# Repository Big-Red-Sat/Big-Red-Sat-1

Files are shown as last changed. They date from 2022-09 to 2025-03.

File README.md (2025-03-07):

# Big Red Sat-1

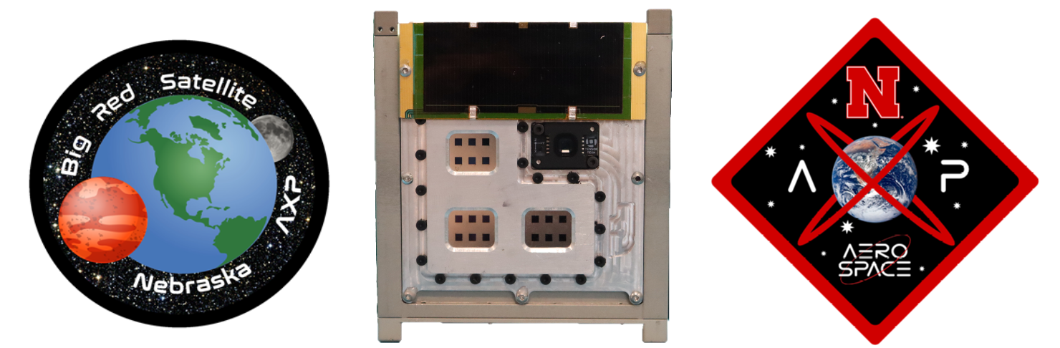
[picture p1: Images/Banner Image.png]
Banner Image


## Introduction 

This repository contains the original designs for the Big Red Sat-1 1U CubeSat, conceived, designed, and launched by a multi-disciplinary team of middle schoolers and high schoolers from the Nebraska public school system, as well as undergraduate students and graduate students from the University of Nebraska-Lincoln.  

The goal of this scientific mission is to characterize the performance and degradation of experimental perovskite solar cells from the National Renewable Energy Laboratory while in low earth orbit.  To accomplish this, a custom precision curve tracer was designed along with a low-Ohm analog multiplexer that was integrated with Near Space Launch's 1U FastBus CubeSat Platform, which incorporates an electrical power system and Iridium satellite communication system for telemetry.  

Electrical connections to the perovskite solar cell samples were made using pogo-pins, with the temperature of each sample being collected with a high-precision temperature sensor affixed to their back face with EP30-2 epoxy.  The enclosure was designed to be airtight to prevent degradation due to humidity and oxygen, so a pressure and humidity sensor were included to monitor changes in this performance.  Since the final samples had a coverslip epoxied to protect the perovskite layer, the airtight property was considered a redundancy.

Big Red Sat-1 was integrated into the Nanoracks CubeSat Deployer 27 (NRCSD27) on 12 December 2023 and launched on 21 March 2024 on the SpaceX CRS-30 mission.   

Big Red Sat-1 was deployed from NRCSD27 by Voyager Space on 18 April 2024 at 18:05:09 UTC ([Deployment Clip](https://www.youtube.com/clip/UgkxD5o3cp39FE0SL8AzyLTBCwdvlqdmNVEa)).  The satellite made first communication with the operations team at 03:00:10 UTC on 19 April 2024.  The satellite deorbited sometime after 23:41:51 UTC on 1 August 2024 after 105 days of operation.

## TLE Data

[Up to date TLE data and visualizations](https://orbit.ing-now.com/satellite/59560/1998-067wk/1998-067wk/)

## Launch Patch

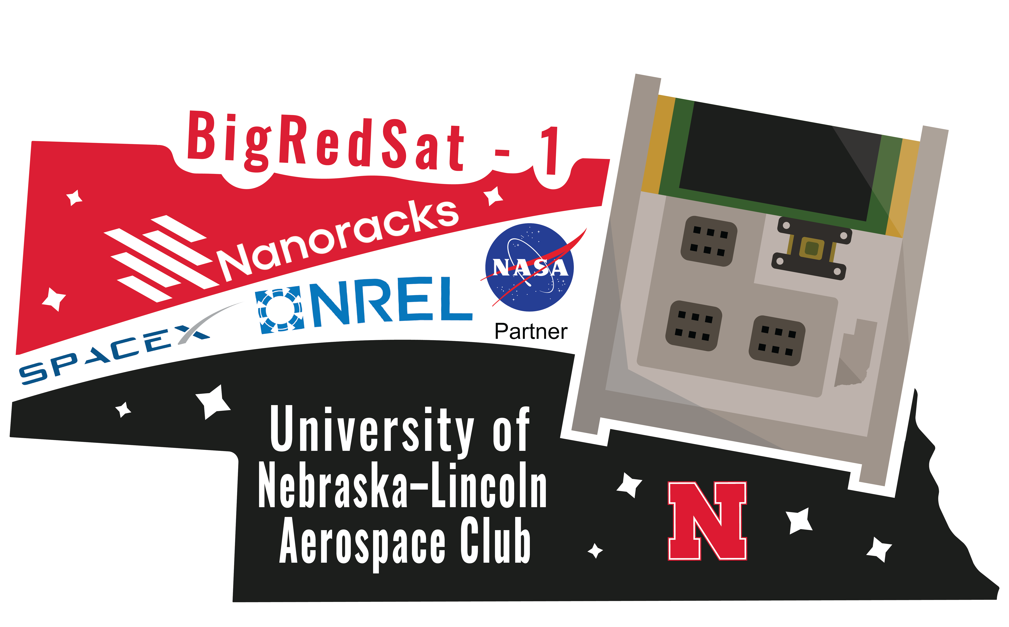
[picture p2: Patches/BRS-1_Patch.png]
BRS-1 Patch


Original concept by Morgan Hurtz, branding by Vince Orsi.

## Current Satellite Location

[SatNOGS DB - Big Red Sat-1](https://db.satnogs.org/satellite/YJQI-7143-2488-2930-9322#mapcontent)

## Prototyping Designs

- [Prototype curve tracers for high altitude balloons](https://github.com/wsarce/Big-Red-Sat-1/tree/main/Prototyping/SIV_pcb)
- [Prototype digital potentiometer curve tracer](https://github.com/wsarce/Big-Red-Sat-1/tree/main/Prototyping/singular_SIV)
- [Prototype resistor ladder curve tracer in LaunchPad form factor](https://github.com/wsarce/Big-Red-Sat-1/tree/main/Prototyping/resistor_ladder_curve_tracer)
- [Prototype analog multiplexer in LaunchPad form factor](https://github.com/wsarce/Big-Red-Sat-1/tree/main/Prototyping/perovskite_switcher/v2)
- [Pressure testing setup with ESP32 and data](https://github.com/wsarce/Big-Red-Sat-1/tree/main/Prototyping/pressure-monitor)
- [Payload breakout board to interact with perovskite cells in payload](https://github.com/wsarce/Big-Red-Sat-1/tree/main/Prototyping/payload-breakout-board/Gecko_Poker)
- [Temperature sensor prototyping](https://github.com/wsarce/Big-Red-Sat-1/tree/main/Prototyping/temp-sensor-prototyping)
- [Neopixel perovskite pixel isolator](https://github.com/wsarce/Big-Red-Sat-1/tree/main/Prototyping/perovskite-cell-isolator)
- [Prototype flight computer with curve tracer and multiplexer](https://github.com/wsarce/Big-Red-Sat-1/tree/main/Prototyping/payload_controller)
- [Magnet mounting jig for orbit alignment magnet](https://github.com/wsarce/Big-Red-Sat-1/tree/main/Prototyping/magnet_mounting)
- [Ossila AM1.5 standoff and mounts](https://github.com/wsarce/Big-Red-Sat-1/tree/main/Prototyping/ossila_mounting)
- [Tooling for building the payload](https://github.com/wsarce/Big-Red-Sat-1/tree/main/Prototyping/payload_mounting)

## Final Designs

- [Flight computer with curve tracer and analog multiplexer](https://github.com/wsarce/Big-Red-Sat-1/tree/main/Flight%20Hardware/flight_computer/v3)
- [Secondary payload with IMU and relay](https://github.com/wsarce/Big-Red-Sat-1/tree/main/Flight%20Hardware/secondary_payload)
- [Tag-Connect programming and data interface](https://github.com/wsarce/Big-Red-Sat-1/tree/main/Flight%20Hardware/Tag%20Connector)
- [Perovskite contact temperature and humiditiy sensor](https://github.com/wsarce/Big-Red-Sat-1/tree/main/Flight%20Hardware/perovskite_contact_board/V7)
- [Perovskite pogo pin board](https://github.com/wsarce/Big-Red-Sat-1/tree/main/Flight%20Hardware/perovskite_contact_board/V6/bot)
- [Perovskite payload enclosure](https://github.com/wsarce/Big-Red-Sat-1/tree/main/Flight%20Payload/Mechanical%20Design)

## Software Developed

- [NSL-EPS-Arduino, an Arduino library to communicate with the NSL electrical power system and radio](https://github.com/wsarce/NSL-EPS-Arduino)
- [FSS100-Arduino, an Arduino library to communicate with the FSS100 sun vector sensor to detect position of sun](https://github.com/wsarce/FSS100-Arduino)
- [pyOssila, a Python library to communicate with the AM1.5 sun simulator](https://github.com/wsarce/pyOssila)
- [Flight firmware for Big Red Sat-1](https://github.com/wsarce/Big-Red-Sat-1/blob/main/Flight%20Hardware/flight_computer/v3/Firmware/brs_flight_firmware/brs_flight_firmware.ino)

## Satellite Exploded View Render

https://github.com/wsarce/Big-Red-Sat-1/assets/22334349/7d4744a6-e3ca-4aac-ab56-a3370dd9aef9

### Contact
For questions, contact either Karen Stelling (kstelling2@unl.edu) or Walker Arce (wsarcera@gmail.com).

### Citation
Arce, W., & Murch-Shafer, J. (2023). Big Red Sat-1 (Version v1.0) [Computer software & hardware]. https://github.com/wsarce/Big-Red-Sat-1

### Funding and Collaboration
This work would not be possible without the generous assistance of our donors and collaborators, listed in alphabetical order below.
1.	Ameritas
2.	Acklie Charitable Foundation
3.	Cooper Foundation
4.	CubeSat Launch Initiative
5.	Ethel S. Abbott Charitable Foundation
6.	Individual Donors
7.	Millard Public Schools Foundation
8.	Monolith
9.	NASA
10.	NASA Nebraska Space Grant
11.	National Renewable Energy Laboratory
12.	Rhodes College
13.	Rodgers Foundation
14.	University of Nebraska-College of Engineering
15.	Oklahoma University

### Media

[April 21, 2021 - NASA selects Nebraska students’ satellite to orbit in space](https://news.unl.edu/newsrooms/today/article/nasa-selects-nebraska-students-satellite-to-orbit-in-space/)

[March 6, 2024 - Big Red Sat Team readies for ISS launch](https://news.unl.edu/newsrooms/today/article/big-red-sat-team-readies-for-iss-launch/)

[March 15, 2024 - Young Nebraska scientists built a satellite, it's now headed to space](https://nebraskapublicmedia.org/en/news/news-articles/young-nebraska-scientists-built-a-satellite-its-now-headed-to-space/)

[March 18, 2024 - NASA Set to Launch Four CubeSats to Space Station](https://blogs.nasa.gov/smallsatellites/2024/03/18/nasa-set-to-launch-four-cubesats-to-space-station/)

[March 21, 2024 - Nebraska students launch satellite into space](https://www.1011now.com/2024/03/21/nebraska-students-launch-satellite-into-space/)

[March 25, 2024 - NASA Space X resupply rocket launches Nebraska CubeSat into outer space](https://engineering.unl.edu/news/240325/nasa_cubesat_launch/)

[March 29, 2024 - Satellite launch a success for Nebraska Engineering team](https://news.unl.edu/newsrooms/today/article/satellite-launch-a-success-for-nebraska-engineering-team/)

[April 22, 2024 - Nebraska's first research satellite reaches International Space Station](https://www.hastingstribune.com/news/nebraskas-first-research-satellite-reaches-international-space-station/article_87f0fb4a-ffdd-11ee-b091-f7073b412070.html)

### Dataset Metadata
The following table is necessary for this dataset to be indexed by search
engines such as <a href="https://g.co/datasetsearch">Google Dataset Search</a>.
<div itemscope itemtype="http://schema.org/Dataset">
<table>
<tr>
<th>property</th>
<th>value</th>
</tr>
<tr>
<td>name</td>
<td><code itemprop="name">Big Red Sat-1 design dataset</code></td>
</tr>
<tr>
<td>description</td>
<td><code itemprop="description">The dataset and designs from the development of the Big Red Sat-1 cube satellite.</code></td>
</tr>
</tr>
<tr>
<td>url</td>
<td><code itemprop="url">https://github.com/wsarce/Big-Red-Sat-1</code></td>
</tr>
<tr>
<td>sameAs</td>
<td><code itemprop="sameAs">https://github.com/wsarce/Big-Red-Sat-1</code></td>
</tr>
<tr>
<td>citation</td>
<td><code itemprop="citation">TBA</code></td>
</tr>
<tr>
<td>hw license</td>
<td>
<div itemscope itemtype="http://schema.org/CreativeWork" itemprop="license">
<table>
<tr>
<th>property</th>
<th>value</th>
</tr>
<tr>
<td>name</td>
<td><code itemprop="name">CERN-OHL-S-2.0</code></td>
</tr>
<tr>
<td>url</td>
<td><code itemprop="url">https://spdx.org/licenses/CERN-OHL-S-2.0.html</code></td>
</tr>
</table>
</div>
</td>
</tr>
<tr>
<td>sw license</td>
<td>
<div itemscope itemtype="http://schema.org/CreativeWork" itemprop="license">
<table>
<tr>
<th>property</th>
<th>value</th>
</tr>
<tr>
<td>name</td>
<td><code itemprop="name">MIT</code></td>
</tr>
<tr>
<td>url</td>
<td><code itemprop="url">https://opensource.org/licenses/MIT</code></td>
</tr>
</table>
</div>
</td>
</tr>
<tr>
<td>docs license</td>
<td>
<div itemscope itemtype="http://schema.org/CreativeWork" itemprop="license">
<table>
<tr>
<th>property</th>
<th>value</th>
</tr>
<tr>
<td>name</td>
<td><code itemprop="name">CC BY-SA 4.0</code></td>
</tr>
<tr>
<td>url</td>
<td><code itemprop="url">https://creativecommons.org/licenses/by-sa/4.0/</code></td>
</tr>
</table>
</div>
</td>
</tr>
</table>
</div>

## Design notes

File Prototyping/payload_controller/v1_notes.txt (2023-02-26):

Each perovskite connection is 2 Ohms
------------------------
Lower resistor values do not help
------------------------
The 0 line of each BCD to decimal decoder will always be on.
To fix this, the 0 lines can be pulled, limiting the decoder to 14 perovskites
The current source and GaAs cell decoder outputs can be pulled and used 
This fix worked, only one output enabled at a time
------------------------
Switch to 4:16 decoder which have inhibit lines (CD4514BM96), tie inhibit line to current enable line
What to do with strobe line?
Break out remaining 12 outputs to an expansion header, create an expansion board that exposes 12 more panel inputs
------------------------
Separate each BCD counter reset to separate I/O pin
------------------------
The ADC clock was probably wrong(?), I used a HCMOS rather than an LVCMOS and the waveform looked terrible on the scope.
Put together new boards, ordered from JLCPCB, and test using a waveform generator and see if that fixes the ADC problems
------------------------
The op amp can't source/sink enough current to drive the panels directly
The negative voltage charge pump can't produce enough current to drive the panel input either
Likely need to use a FET with op amp for feedback to control a voltage source into the panel
I don't think this will be working in time for the cubesat
Otherwise, the DAC works well, the voltage source generation (-0.3 to 1.2) works correctly, and the charge pump works with low load.
SIT8924BA-22-33E-8.192000 is the clock used by the eval kit from TI
------------------------
I have a board that will work for the vibration testing, but I need to clear up these other problems first
------------------------

Panel 1: Cell 3
Panel 2: Cell 1
Panel 3: Cell 7
Panel 4: Cell 2
Panel 5: Cell 4
Panel 6: Cell 5
Panel 7: Cell 15
Panel 8: Cell 6
Panel 9: Cell 16

Panel 12: Cell 13
Panel 13: Cell 18
Panel 14: Cell 14
Panel 15: Cell 17
Panel 16: Cell 10
Panel 17: Cell 9
Panel 18: Cell 12
Panel 19: Cell 8
Panel 20: Cell 11

------------------------

It looks like when the COM node is the positive lead, there is influence from the other panels on the target panel.  This could probably be compensated for by connecting the bottom of the voltage divider to 3V3, so that it shifts negative voltages up to positive.  This would allow that fix.

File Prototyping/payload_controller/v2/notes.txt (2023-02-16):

Add FRAM chip to store data, calibration, etc etc.? Those chips are expensive but it may be useful for timing transmissions

Remove low pass filter on current and voltage inputs to ADC... maybe?

Create grounded border

0.5 mm box header for JTAG

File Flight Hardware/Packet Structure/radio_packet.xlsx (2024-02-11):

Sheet: Packet Structure
Byte | Primary Packet | Secondary Packet
1 | Phi MSB | Phi StD MSB |  | status register | 7 | 6 | 5 | 4 | 3 | 2 | 1 | 0
2 | Phi LSB | Phi StD LSB |  |  |  |  |  | pixel | pixel | pixel | pixel | pixel
3 | Theta MSB | Theta StD NSB
4 | Theta LSB | Theta StD LSB | Temp StD MSB
5 | Temp MSB | Rotation Rate | Temp StD LSB
6 | Temp LSB | Rotation Rate StD
7 | Status Register | Boot count | Bit 7 for relay, Bit 6 for orbit samples,
8 | Vsc | Relay Voltage |  |  |  | Multiply v and I, find max power point from trace, send point before and after that
9 | Isc | Ax
10 | V2 | Ay
11 | I2 | Az
12 | V3 | Mx
13 | I3 | My
14 | V4 | Mz
15 | I4 |  | LK99 Resistance??
16 | Voc | battery level?? | 0xBE
17 | Ioc | 0xEF
 | Write zeroes to failed fields
 | boot count should overflow in ~16 days
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

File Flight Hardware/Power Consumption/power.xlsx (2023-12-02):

Domain
3V3 | 3 | mA
VBUS | 4 | mA
VDDF | 2.8 | mA
VPP | 0.003 | mA
 | 9.803
Battery

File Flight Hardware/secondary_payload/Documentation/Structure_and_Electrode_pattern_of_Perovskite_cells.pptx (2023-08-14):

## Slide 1

Ce

Ce

MoOx (15 nm)

Au (100 nm)

Triple Cation
Perovskite Cells

Ce

Ce

MoOx (15 nm)

Au (100 nm)

Ce

SPIRO (150 nm)

Ce

SPIRO (150 nm)

Ce

Ce

Triple Cation (500 nm)

Ce

Triple Cation (500 nm)

Ce

SnO2 (50 nm)

ITO (150 nm)

Ce

Ce

SnO2 (50 nm)

ITO (150 nm)

Ce

Ce-Borosilicate (250 μm)

Ce

Fused Silica (1000 μm)

Ce

Al (100 nm)

Ce

Al (100 nm)

Ce

MoOx (15 nm)

Ce

MoOx (15 nm)

Ce

Ce

Triple Cation (500 nm)

PTAA (30 nm)

Ce

SPIRO (150 nm)

Ce

SnO2 (50 nm)

Ce

Ce

Triple Cation (500 nm)

SnO2 (50 nm)

Ce

ITO (150 nm)

Ce

ITO (150 nm)

Ce

Soda Lime Glass (1000 μm)

Ce

Soda Lime Glass (1000 μm)

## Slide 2

Ce

Ce

MoOx (15 nm)

Al (100 nm)

All-Inorganic
Perovskite Cells

Ce

Ce

MoOx (15 nm)

Au (100 nm)

Ce

PTAA (30 nm)

Ce

SPIRO (150 nm)

Ce

Ce

CsPbI2Br (250 nm)

Ce

CsPbI2Br (250 nm)

Ce

SnO2 (50 nm)

ITO (150 nm)

Ce

Ce

SnO2 (50 nm)

ITO (150 nm)

Ce

Soda Lime Glass (1000 μm)

Ce

Ce-Borosilicate (250 μm)

Ce

Au (100 nm)

Ce

Al (100 nm)

Ce

MoOx (15 nm)

Ce

MoOx (15 nm)

Ce

SPIRO (150 nm)

Ce

Ce

CsPbI2Br (250 nm)

SPIRO (150 nm)

Ce

Ce

CsPbI2Br (250 nm)

SnO2 (50 nm)

Ce

SnO2 (50 nm)

Ce

ITO (150 nm)

Ce

ITO (150 nm)

Ce

Fused Silica (1000 μm)

Ce

Soda Lime Glass (1000 μm)

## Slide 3

Electrode pattern on the solar cell

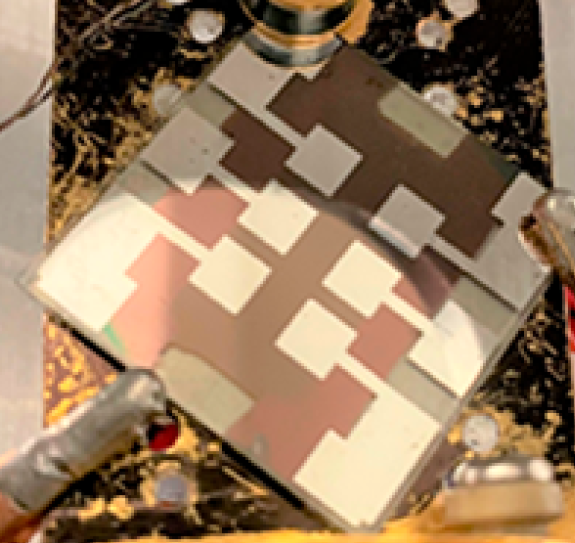
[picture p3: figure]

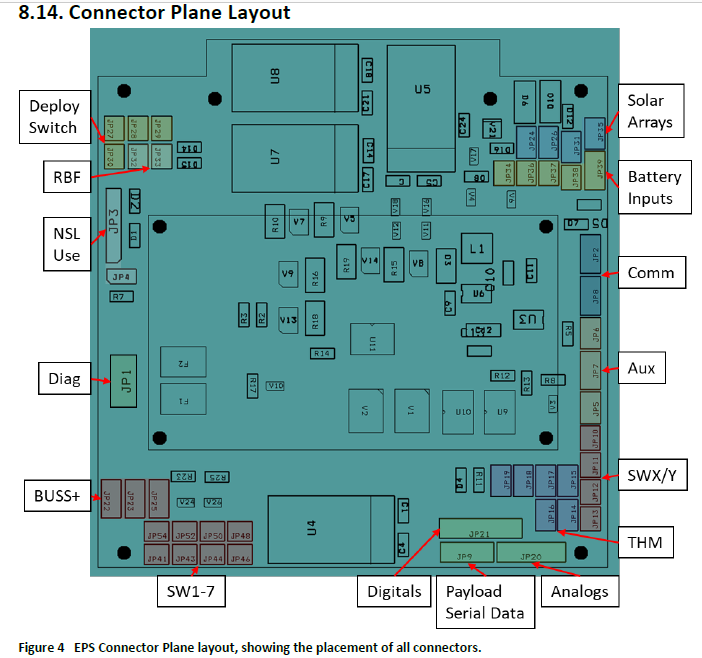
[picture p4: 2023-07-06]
Flight Hardware/secondary_payload/Documentation/Connector Specs/Connector Plane Layout.PNG

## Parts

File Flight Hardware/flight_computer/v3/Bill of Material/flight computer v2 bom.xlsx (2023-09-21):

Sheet: SMD Components
Ref | Quantity | Value | Footprint | Rating | Vendor
C1, C10, C100, C106, C109, | 5 | 10u | Capacitor_SMD:C_0603_1608Metric | AEC-Q200 | https://www.digikey.com/en/products/detail/kyocera-avx/KAM15CT70J106KT/17634162
C2, C4, C5, C6, C9, C11, C14, C15, C16, C17, C18, C19, C20, C21, C22, C23, C28, C29, C51, C52, C53, C54, C55, C56, C57, C58, C59, C60, C61, C62, C63, C64, C65, C66, C67, C68, C69, C70, C71, C74, C75, C76, C77, C78, C79, C80, C81, C82, C83, C84, C85, C86, C88, C89, C90, C91, C92, C93, C96, C97, C99, C101, C104, C107, C110, C111, | 66 | 0.1u | Capacitor_SMD:C_0603_1608Metric | COTS | https://www.digikey.com/en/products/detail/kemet/C0603T104K5RAC7867/12700990
C3, C7, C46, C47, C48, | 5 | 1u | Capacitor_SMD:C_0603_1608Metric | AEC-Q200 | https://www.digikey.com/en/products/detail/tdk-corporation/CGA3E1X7R1C105K080AC/3949775
C8, C105, C108, | 3 | 47u | Capacitor_Tantalum_SMD:CP_EIA-7343-43_Kemet-X | COTS | https://www.digikey.com/en/products/detail/kemet/T541X227M016AH6710/3478654
C12, C13, | 2 | 10p | Capacitor_SMD:C_0603_1608Metric | COTS | https://www.digikey.com/en/products/detail/kemet/C0603T100J5GAC7867/9924899
C24, C25, C26, C27, C32, C33, C34, C35, C42, | 9 | 10n | Capacitor_SMD:C_0603_1608Metric | COTS | https://www.digikey.com/en/products/detail/kemet/C0603T103K5RCL7867/2202506
FB1, | 1 | Ferrite_Bead_Small | Inductor_SMD:L_0603_1608Metric | AEC-Q200 | https://www.digikey.com/en/products/detail/tdk-corporation/MPZ1608S601ATD25/5040321
R1, R2, | 2 | 4k7 | Resistor_SMD:R_0603_1608Metric | AEC-Q200 | https://www.digikey.com/en/products/detail/vishay-dale/TNPW06034K70BEEA/1606843
R3, R71, R72, R73, R74, R75, R76, R77, R78, R80, | 10 | 10k | Resistor_SMD:R_0603_1608Metric | "Military" | https://www.digikey.com/en/products/detail/vishay-dale/TNPW060310K0FHTA/7354881
R4, R5, R6, R7, R8, R9, R14, R15, R22, R23, R24, R25, R30, R31, R42, R43, R46, | 17 | 470 | Resistor_SMD:R_0603_1608Metric | AEC-Q200 | https://www.digikey.com/en/products/detail/susumu/RG1608P-471-B-T5/1240592
R16, R17, R32, R33, R52, | 5 | 510m | Resistor_SMD:R_1206_3216Metric | AEC-Q200 | https://www.digikey.com/en/products/detail/koa-speer-electronics-inc/SR732BTTDR51J/12749611?s=N4IgTCBcDaIMoCUDsBmMAhAKpgIggrAIwBSIAugL5A
R18, R19, R20, R21, R34, R35, R36, R37, | 8 | 10M | Resistor_SMD:R_0603_1608Metric | AEC-Q200 | https://www.digikey.com/en/products/detail/vishay-dale/CRCW060310M0FHEAP/5070695
R55, R59, R63, R67, | 4 | 120 | Resistor_SMD:R_0603_1608Metric | AEC-Q200 | https://www.digikey.com/en/products/detail/susumu/RG1608N-121-W-T1/600575
R56, R60, R64, R68, | 4 | 270 | Resistor_SMD:R_0603_1608Metric | AEC-Q200 | https://www.digikey.com/en/products/detail/susumu/RG1608N-271-W-T1/600583
R57, R61, R65, R69, | 4 | 430 | Resistor_SMD:R_0603_1608Metric | AEC-Q200 | https://www.digikey.com/en/products/detail/susumu/RG1608N-431-W-T1/600588
R58, R62, R66, R70, R79, | 5 | 1M | Resistor_SMD:R_0603_1608Metric | AEC-Q200 | https://www.digikey.com/en/products/detail/rohm-semiconductor/ESR03EZPF1004/4007144
R81, | 1 | 3M | Resistor_SMD:R_0603_1608Metric | AEC-Q200 | https://www.digikey.com/en/products/detail/rohm-semiconductor/KTR03EZPF3004/4051626
Y1, | 1 | CM8V-T1A | CM8V-T1A-32:XTAL_CM8V-T1A-32.768KHZ-7PF-20PPM-TA-QC | AEC-Q200 | https://www.digikey.com/en/products/detail/jauch-quartz/Q-0-032768-JTX310-7-10-T3-HMR-LF/8108094
J5, | 1 | Panel 3 Input | Connector_Hirose:Hirose_DF13C_CL535-0403-5-51_1x03-1MP_P1.25mm_Vertical |  | https://www.digikey.com/en/products/detail/hirose-electric-co-ltd/DF13C-3P-1-25V-21/3907689
J8, | 1 | Panel 3 Output | Connector_Hirose:Hirose_DF13C_CL535-0403-5-51_1x03-1MP_P1.25mm_Vertical |  | https://www.digikey.com/en/products/detail/hirose-electric-co-ltd/DF13C-3P-1-25V-21/3907689
J9, | 1 | Sun Vector Sensor | 0781710004:MOLEX_0781710004 |  | https://www.digikey.com/en/products/detail/molex/0781710004/2424925?s=N4IgTCBcDaIOwA4CMckAYMBYQF0C%2BQA
J11, | 1 | GaAs Panel | Connector_Hirose:Hirose_DF13C_CL535-0403-5-51_1x03-1MP_P1.25mm_Vertical |  | https://www.digikey.com/en/products/detail/hirose-electric-co-ltd/DF13C-3P-1-25V-21/3907689
J12, | 1 | GaAs Temperature | Connector_Hirose:Hirose_DF13C_CL535-0403-5-51_1x03-1MP_P1.25mm_Vertical |  | https://www.digikey.com/en/products/detail/hirose-electric-co-ltd/DF13C-3P-1-25V-21/3907689
J15, J16, J18, J19, J22, | 5 | Power | Connector_Hirose:Hirose_DF13C_CL535-0402-2-51_1x02-1MP_P1.25mm_Vertical |  | https://www.digikey.com/en/products/detail/hirose-electric-co-ltd/DF13-2P-1-25V-76/9170624
J20, | 1 | BUSS+ | Connector_Hirose:Hirose_DF13C_CL535-0404-8-51_1x04-1MP_P1.25mm_Vertical |  | https://www.digikey.com/en/products/detail/hirose-electric-co-ltd/DF13C-4P-1-25V-51/3977746
J21, | 1 | EPS Serial | Connector_Hirose:Hirose_DF13C_CL535-0406-3-51_1x06-1MP_P1.25mm_Vertical |  | https://www.digikey.com/en/products/detail/hirose-electric-co-ltd/DF13B-6P-1-25V-51/3977725
Q1, Q2, Q3, | 3 | BSS138 | Package_TO_SOT_SMD:SOT-23 |  | https://www.digikey.com/en/products/detail/anbon-semiconductor-int-l-limited/BSS138/16708474
U1, U2, | 2 | OPA2387 | Package_SO:VSSOP-8_3.0x3.0mm_P0.65mm |  | https://www.digikey.com/en/products/detail/texas-instruments/OPA2387DGKR/13627209
U3, U10, | 2 | TLV7031DBV | Package_TO_SOT_SMD:SOT-23-5 |  | https://www.digikey.com/en/products/detail/texas-instruments/TLV7031DBVR/10434768?s=N4IgTCBcDaICoBkBqB2ADAZgIwBEBCSIAugL5A
U6, | 1 | CD4012BPWR | Package_SO:TSSOP-14_4.4x5mm_P0.65mm |  | https://www.digikey.com/en/products/detail/texas-instruments/CD4012BPWR/1690715
U7, | 1 | LT6654AHS6-3.3 | Package_TO_SOT_SMD:SOT-23-6 |  | https://www.digikey.com/en/products/detail/analog-devices-inc/LT6654AHS6-3-3-TRMPBF/2485815
U8, | 1 | M4FR5969SPHPT-MLS | Package_QFP:LQFP-48_7x7mm_P0.5mm | Radiation Hardened | https://www.digikey.com/en/products/detail/texas-instruments/M4FR5969SPHPT-MLS/9860026
U9, | 1 | 74CBTLV3253PW,118 | Package_SO:TSSOP-16_4.4x5mm_P0.65mm |  | https://www.digikey.com/en/products/detail/nexperia-usa-inc/74CBTLV3253PW-118/2530383
U11, U12, U13, U14, U17, | 5 | INA190A4IDDFR | ul_INA190A4IDDFR:INA190A4IDDFR |  | https://www.digikey.com/en/products/detail/texas-instruments/INA190A4IDDFR/11308738?s=N4IgTCBcDaIJIDkCCBGAnABiQFjgETwDEAlEAXQF8g
U18, U19, U20, U22, U23, U24, U25, U27, U28, U29, U30, U32, U33, U34, U35, U37, | 16 | ADG841YKSZ-500RL7 | ul_ADG841YKSZ-500RL7:ADG841YKSZ-500RL7 |  | https://www.digikey.com/en/products/detail/analog-devices-inc/ADG841YKSZ-500RL7/995409
U21, U26, U31, U36, | 4 | CD4516B_PW_16 | Package_SO:TSSOP-16_4.4x5mm_P0.65mm |  | https://www.digikey.com/en/products/detail/texas-instruments/CD4516BPW/1691567
U38, | 1 | CD4518BM96 | ul_CD4518BM96:CD4518BM96 |  | https://www.digikey.com/en/products/detail/texas-instruments/CD4520BM96/1691583
U39, | 1 | 74AHC1G08 | Package_TO_SOT_SMD:SOT-23-5 |  | https://www.digikey.com/en/products/detail/texas-instruments/SN74AHC1G08DBVR/276735
U40, U41, | 2 | CD4514BM | ul_CD4514BM:CD4514BM |  | https://www.digikey.com/en/products/detail/texas-instruments/CD4514BM/528397
U42, U43, U44, U45, U46, U47, U48, U49, U50, U51, U52, U53, U54, U55, U56, U57, U58, U59, | 18 | ADG839YKSZ-REEL7 | ul_ADG839YKSZ-REEL7:ADG839YKSZ-REEL7 |  | https://www.digikey.com/en/products/detail/analog-devices-inc/ADG839YKSZ-REEL7/995410

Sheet: THT Components
Ref | Quantity | Value | Footprint | Vendor
J10, | 1 | Perovskite 3 | Connector_Molex:Molex_PicoBlade_53047-1110_1x11_P1.25mm_Vertical | https://www.digikey.com/en/products/detail/hirose-electric-co-ltd/DF13-11P-1-25DSA-05/15997313
J13, | 1 | Perovskite 1 | Connector_Molex:Molex_PicoBlade_53047-1110_1x11_P1.25mm_Vertical | https://www.digikey.com/en/products/detail/hirose-electric-co-ltd/DF13-11P-1-25DSA-05/15997313
J14, | 1 | Perovskite 2 | Connector_Molex:Molex_PicoBlade_53047-1110_1x11_P1.25mm_Vertical | https://www.digikey.com/en/products/detail/hirose-electric-co-ltd/DF13-11P-1-25DSA-05/15997313
J3, | 1 | Secondary Payload | Connector_Molex:Molex_PicoBlade_53047-1010_1x10_P1.25mm_Vertical | https://www.digikey.com/en/products/detail/molex/0530471010/242861
J1, J2, | 2 | External Debug | Connector_Molex:Molex_PicoBlade_53047-0510_1x05_P1.25mm_Vertical | https://www.digikey.com/en/products/detail/molex/0530470510/242856

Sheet: Cable Harnesses
Item | Quantity | Length (mm) | Link
External debug cables | 2 | 100 | https://www.digikey.com/en/products/detail/molex/0151340501/6198151
Secondary payload | 1 | 100 | https://www.digikey.com/en/products/detail/molex/0151341001/7928364
Perovskite connector | 3 | 0 | https://www.digikey.com/en/products/detail/hirose-electric-co-ltd/DF13-11S-1-25C/241760

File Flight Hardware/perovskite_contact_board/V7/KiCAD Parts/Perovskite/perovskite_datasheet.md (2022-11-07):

Sourced from Oklahoma University

Exposure to oxygen and moisture will cause an increased rate of degradation

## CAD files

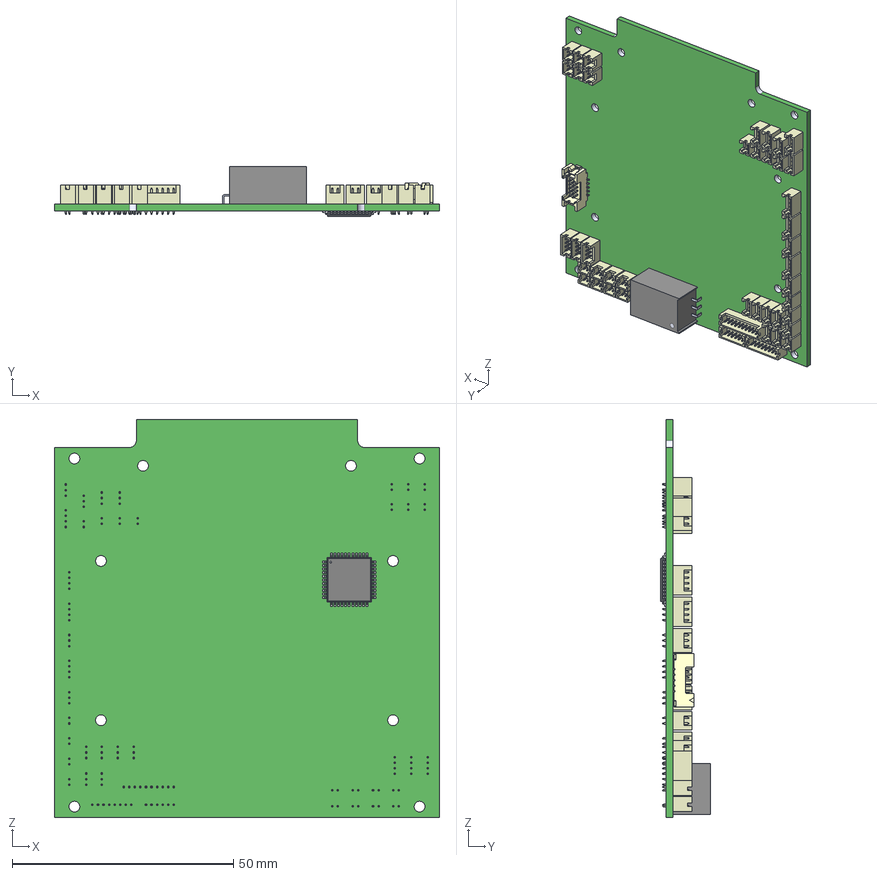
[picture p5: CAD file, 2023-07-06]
Flight Hardware/flight_computer/v3/Documentation/Connector Specs/EPS PCB Asm v17.STEP.STEP.step
87.0 x 11.3 x 90.0 mm
DF13-2P-1.25DSA.1.step.STEP x 22
DF13-3P-1.25DSA.step.STEP x 12
DF13-4P-1.25DSA.step.STEP x 7
DF13-6P-1.25DSA.step.STEP
DF13-10P-1.25DSA.step.STEP
DF13-8P-1.25DSA.step.STEP
1U EPS Board v17.step.STEP
R78B5.0-1.0L.step.STEP
DF13EA-10DP-1.25V.step.STEP
TQFP44_MC.step.STEP

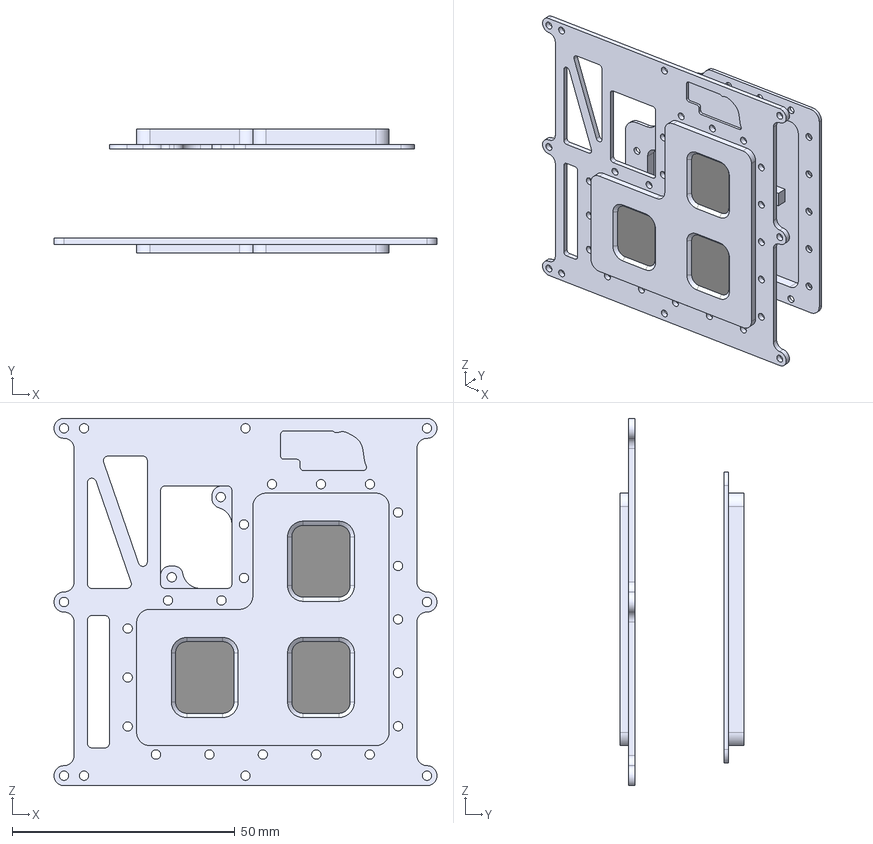
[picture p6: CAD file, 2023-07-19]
Flight Hardware/perovskite_contact_board/V7/assembly.step
86.0 x 27.9 x 82.5 mm
PayloadRedesignFinalTop
PayloadRedesignFinalBottom

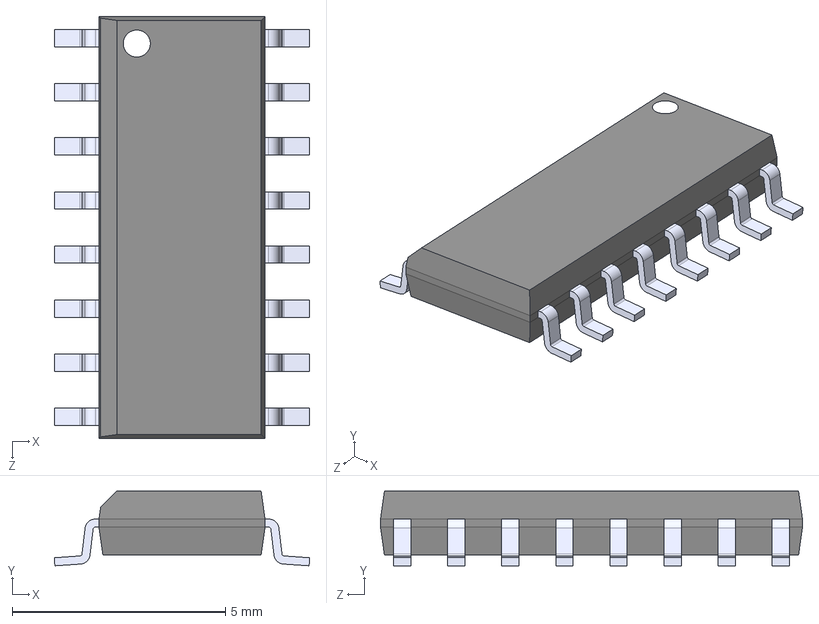
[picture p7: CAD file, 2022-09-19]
boost_converter_curve_tracer/KiCAD Parts/CD4028BMT/CD4028BMT.step
5.99 x 1.75 x 9.91 mm

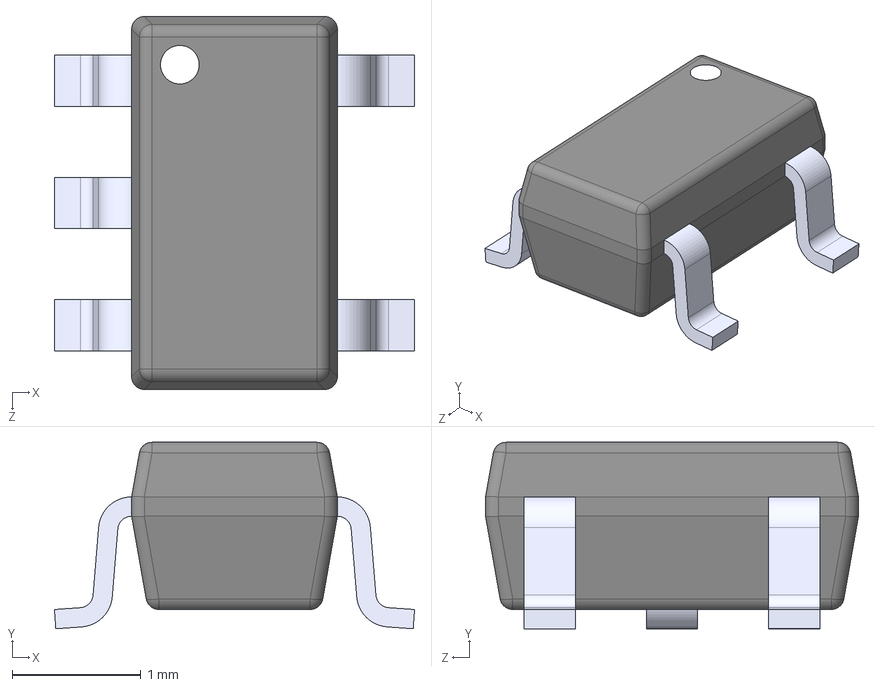
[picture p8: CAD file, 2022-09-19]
boost_converter_curve_tracer/KiCAD Parts/INA180B2IDBVT/INA180B2IDBVT.step
2.80 x 1.45 x 2.90 mm

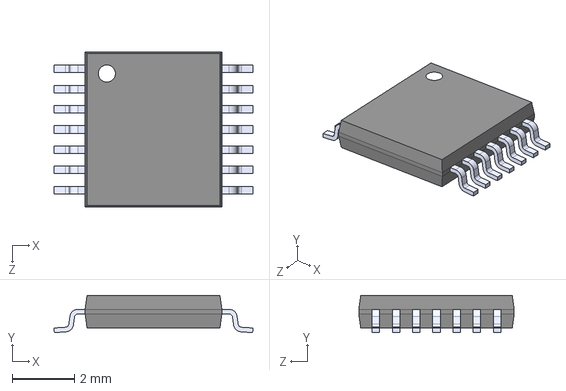
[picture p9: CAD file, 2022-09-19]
boost_converter_curve_tracer/KiCAD Parts/INA4180A4IPWR/INA4180A4IPWR.step
6.40 x 1.20 x 5.00 mm

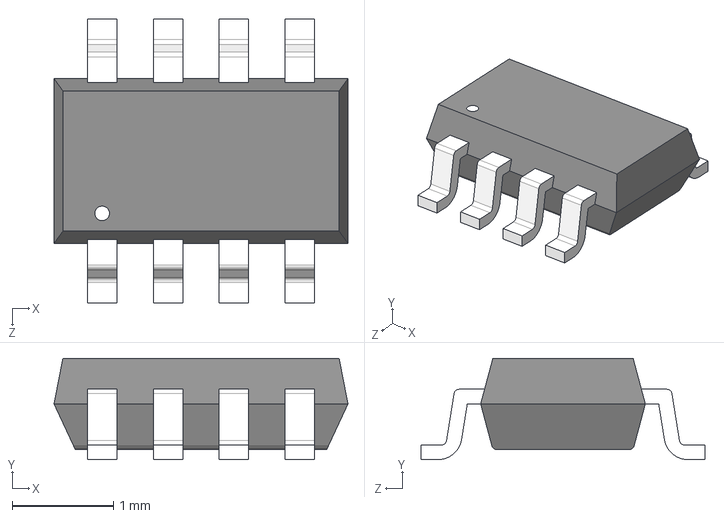
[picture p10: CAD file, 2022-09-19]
boost_converter_curve_tracer/KiCAD Parts/LT3092ETS8TRPBF/LT3092ETS8TRPBF.step
2.90 x 1.00 x 2.80 mm

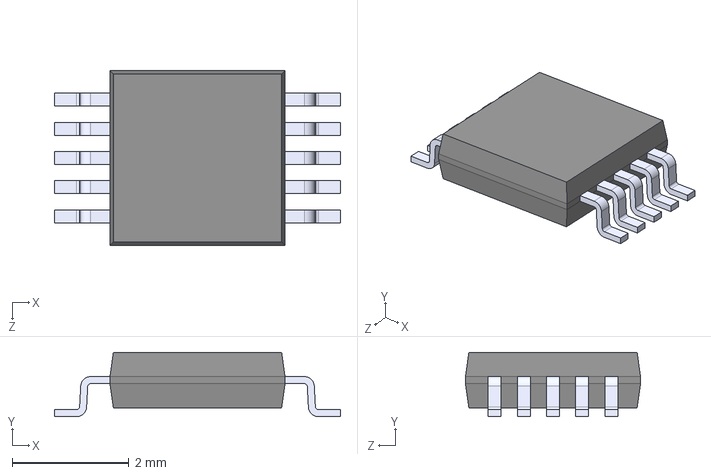
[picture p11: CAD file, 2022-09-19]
boost_converter_curve_tracer/KiCAD Parts/MAX4736EUBT/MAX4736EUBT.step
4.90 x 1.10 x 3.00 mm

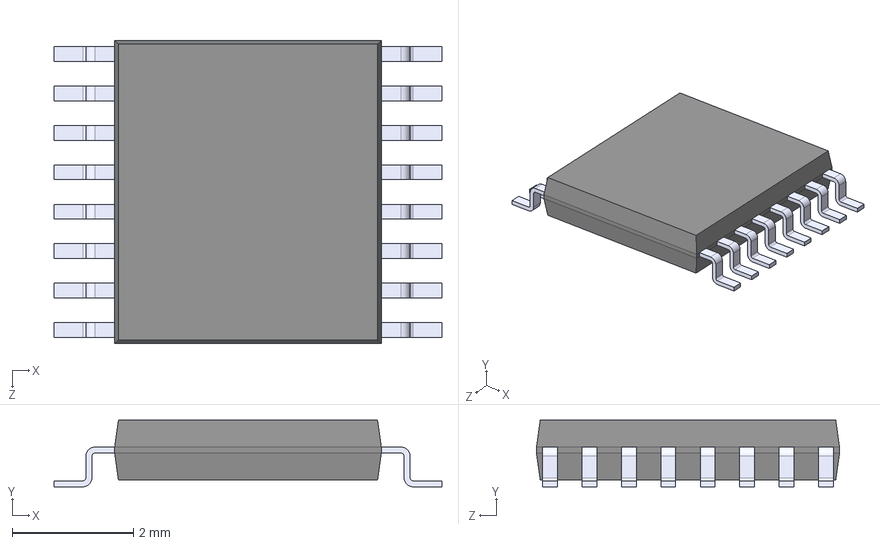
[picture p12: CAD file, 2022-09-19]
boost_converter_curve_tracer/KiCAD Parts/NX3L4051PW_118/NX3L4051PW_118.step
6.40 x 1.10 x 5.00 mm

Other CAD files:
Flight Hardware/Tag Connector/Tag Connector.step
Flight Hardware/flight_computer/v1/KiCAD Parts/LIB_G125-MH12605M4R/G125-MH12605M4R.stp
Flight Hardware/flight_computer/v1/KiCAD Parts/LIB_G125-MV12605M1P/G125-MV12605M1P.stp
Flight Hardware/flight_computer/v2/Board Outline/Cubesat_FL_Board.step
Flight Hardware/flight_computer/v2/Board Outline/final_outline.dxf
Flight Hardware/flight_computer/v2/KiCAD Parts/530471110/530471110.stp
Flight Hardware/flight_computer/v2/KiCAD Parts/LIB_G125-MH12605M4R/G125-MH12605M4R.stp
Flight Hardware/flight_computer/v2/KiCAD Parts/LIB_G125-MV12605M1P/G125-MV12605M1P.stp
Flight Hardware/flight_computer/v3/Board Outline/Cubesat_FL_Board.step
Flight Hardware/flight_computer/v3/Board Outline/final_outline.dxf
Flight Hardware/flight_computer/v3/KiCAD Parts/530471110/530471110.stp
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

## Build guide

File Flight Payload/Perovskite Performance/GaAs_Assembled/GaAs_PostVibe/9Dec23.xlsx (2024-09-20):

 | FF | VOC | JSC | Eff | ISC | MPP_V | MPP_I | MPP_P | Pixel | Sample | Direction
0 | 65.05564388 | 5728.470588 | 1.576485922 | 5.87507972 | 32.25490196 | 5.109176471 | 23.52710496 | 120.2041311 | 0 | GaAs | Reverse
1 | 72.67267267 | 5728.470588 | 1.576485922 | 6.562962412 | 32.25490196 | 5.676862745 | 23.65359477 | 134278.2109 | 0 | GaAs | Forward

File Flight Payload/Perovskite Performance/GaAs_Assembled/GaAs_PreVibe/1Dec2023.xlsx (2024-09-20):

 | FF | VOC | JSC | Eff | ISC | MPP_V | MPP_I | MPP_P | Pixel | Sample | Direction
0 | 65.82633053 | 5780.078431 | 1.576485922 | 5.99823497 | 32.25490196 | 5.160784314 | 23.78008458 | 122.7238875 | 0 | GaAs | Reverse
1 | 73.45588235 | 5780.078431 | 1.576485922 | 6.693455928 | 32.25490196 | 5.728470588 | 23.90657439 | 136948.1083 | 0 | GaAs | Forward

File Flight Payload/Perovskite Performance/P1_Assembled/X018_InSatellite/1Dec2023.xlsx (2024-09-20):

 | FF | VOC | JSC | Eff | ISC | MPP_V | MPP_I | MPP_P | Pixel | Sample | Direction
0 | 54.16666667 | 928.9411765 | 32.71288231 | 16.46035267 | 1.897347174 | 0.5031764706 | 1.897347174 | 0.9547004546 | 0 | X018 | Reverse
1 | 66.96428571 | 825.7254902 | 30.53202349 | 16.88241299 | 1.770857363 | 0.5160784314 | 1.897347174 | 979.1799534 | 0 | X018 | Forward
2 | 65.91549296 | 916.0392157 | 32.71288231 | 19.7524232 | 1.897347174 | 0.6967058824 | 1.644367551 | 1.145640545 | 1 | X018 | Reverse
3 | 87.5 | 825.7254902 | 30.53202349 | 22.05968631 | 1.770857363 | 0.7225098039 | 1.770857363 | 1279.461806 | 1 | X018 | Forward
4 | 68.6888454 | 941.8431373 | 30.53202349 | 19.7524232 | 1.770857363 | 0.6967058824 | 1.644367551 | 1.145640545 | 2 | X018 | Reverse
5 | 81.25 | 825.7254902 | 30.53202349 | 20.48399443 | 1.770857363 | 0.7225098039 | 1.644367551 | 1188.071677 | 2 | X018 | Forward
6 | 62.77665996 | 916.0392157 | 30.53202349 | 17.55770951 | 1.770857363 | 0.6709019608 | 1.517877739 | 1.018347152 | 3 | X018 | Reverse
7 | 80.87557604 | 799.9215686 | 30.53202349 | 19.7524232 | 1.770857363 | 0.6967058824 | 1.644367551 | 1145.640545 | 3 | X018 | Forward
8 | 63.98390342 | 916.0392157 | 30.53202349 | 17.89535777 | 1.770857363 | 0.6838039216 | 1.517877739 | 1.037930751 | 4 | X018 | Reverse
9 | 79.24297924 | 812.8235294 | 28.35116467 | 18.26114338 | 1.644367551 | 0.7612156863 | 1.391387928 | 1059.146316 | 4 | X018 | Forward
10 | 63.22444679 | 941.8431373 | 28.35116467 | 16.88241299 | 1.644367551 | 0.6450980392 | 1.517877739 | 0.9791799534 | 5 | X018 | Reverse
11 | 71.66276347 | 787.0196078 | 30.53202349 | 17.22006125 | 1.770857363 | 0.658 | 1.517877739 | 998.7635525 | 5 | X018 | Forward

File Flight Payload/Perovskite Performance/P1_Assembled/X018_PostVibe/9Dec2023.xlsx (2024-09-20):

 | FF | VOC | JSC | Eff | ISC | MPP_V | MPP_I | MPP_P | Pixel | Sample | Direction
0 | 65.78947368 | 980.5490196 | 26.17030585 | 16.88241299 | 1.517877739 | 0.6450980392 | 1.517877739 | 0.9791799534 | 0 | X018 | Reverse
1 | 81.94444444 | 851.5294118 | 26.17030585 | 18.26114338 | 1.517877739 | 0.7612156863 | 1.391387928 | 1059.146316 | 0 | X018 | Forward
2 | 72.07207207 | 954.745098 | 26.17030585 | 18.00790719 | 1.517877739 | 0.8257254902 | 1.264898116 | 1.044458617 | 1 | X018 | Reverse
3 | 79.88980716 | 851.5294118 | 23.98944703 | 16.31966589 | 1.391387928 | 0.7483137255 | 1.264898116 | 946.5406216 | 1 | X018 | Forward
4 | 68.18181818 | 980.5490196 | 23.98944703 | 16.03829234 | 1.391387928 | 0.7354117647 | 1.264898116 | 0.9302209557 | 2 | X018 | Reverse
5 | 79.88980716 | 851.5294118 | 23.98944703 | 16.31966589 | 1.391387928 | 0.7483137255 | 1.264898116 | 946.5406216 | 2 | X018 | Forward
6 | 65.43589744 | 967.6470588 | 28.35116467 | 17.95163248 | 1.644367551 | 0.7483137255 | 1.391387928 | 1.041194684 | 3 | X018 | Reverse
7 | 83.20512821 | 838.627451 | 26.17030585 | 18.26114338 | 1.517877739 | 0.7612156863 | 1.391387928 | 1059.146316 | 3 | X018 | Forward
8 | 71.84684685 | 954.745098 | 26.17030585 | 17.95163248 | 1.517877739 | 0.7483137255 | 1.391387928 | 1.041194684 | 4 | X018 | Reverse
9 | 74.49494949 | 851.5294118 | 26.17030585 | 16.60103944 | 1.517877739 | 0.7612156863 | 1.264898116 | 962.8602875 | 4 | X018 | Forward
10 | 59.21052632 | 980.5490196 | 26.17030585 | 15.19417169 | 1.517877739 | 0.6967058824 | 1.264898116 | 0.8812619581 | 5 | X018 | Reverse
11 | 73.92473118 | 799.9215686 | 26.17030585 | 15.47554524 | 1.517877739 | 0.7096078431 | 1.264898116 | 897.581624 | 5 | X018 | Forward

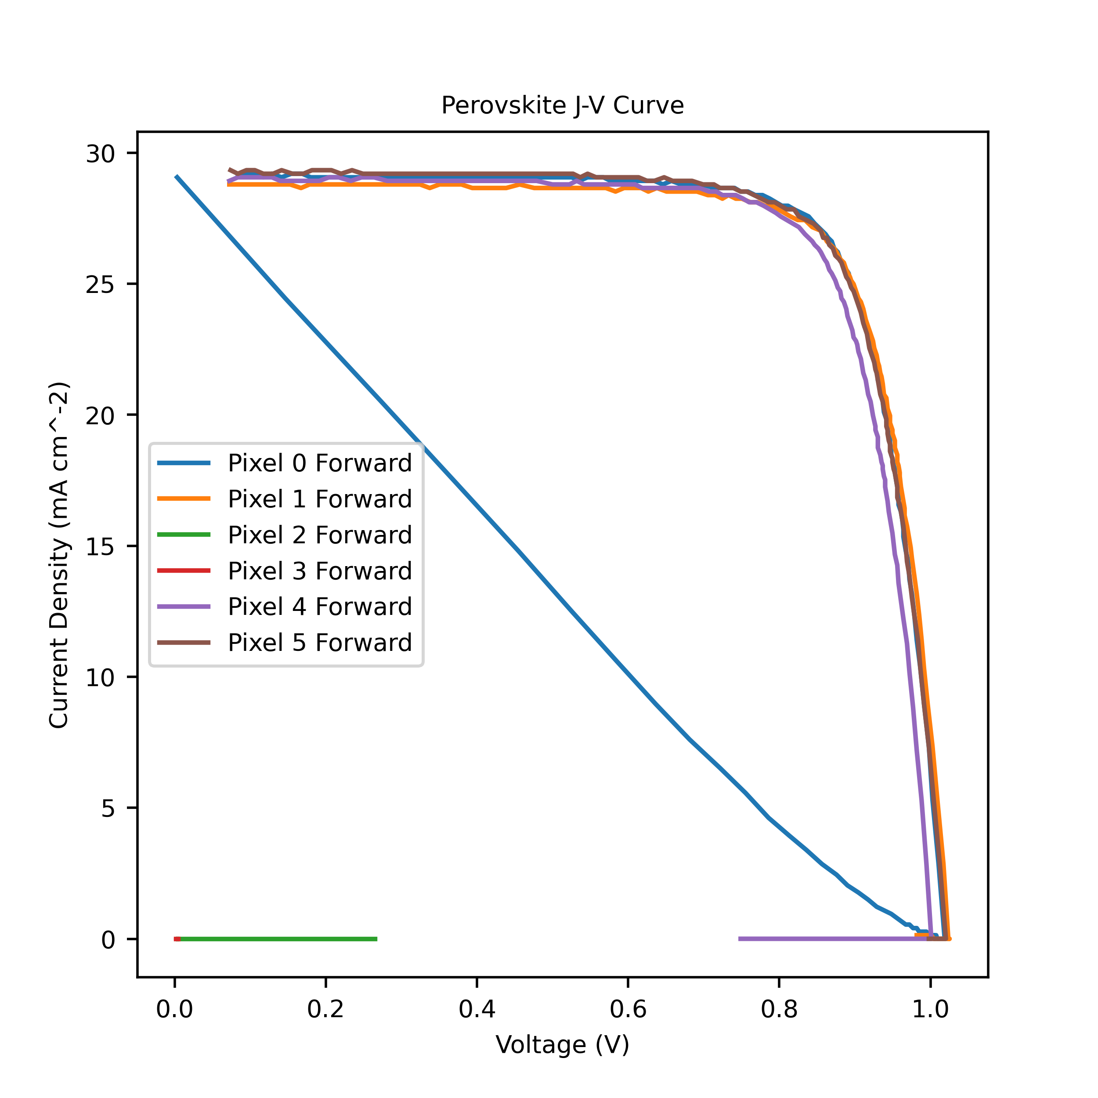
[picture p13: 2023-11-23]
Flight Payload/Perovskite Performance/P2_Assembled/X016_PreSatellite/X016_Payload2_FinalCurves_plotted_Forward.png

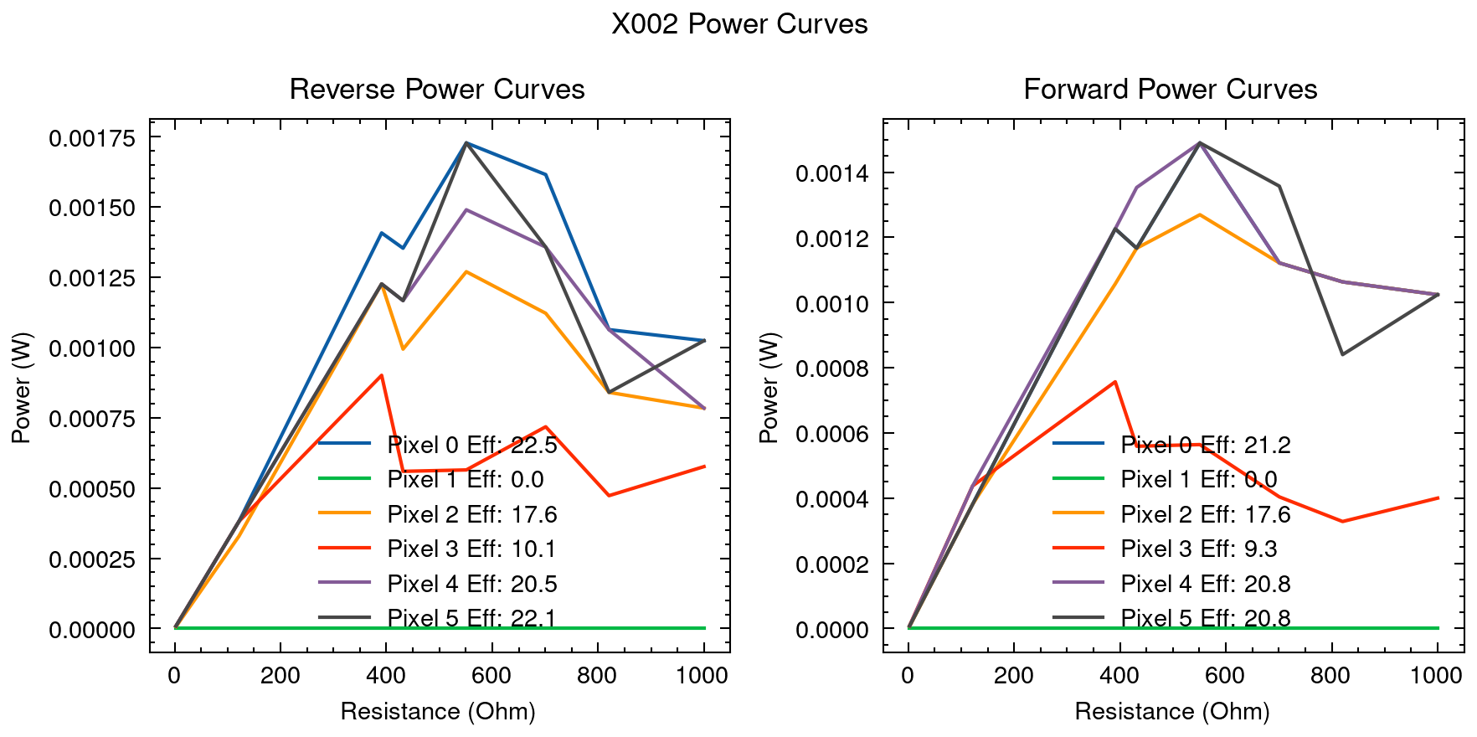
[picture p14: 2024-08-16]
Flight Payload/Perovskite Performance/P3_Assembled/X002_InSatellite/1Dec2023_power.png

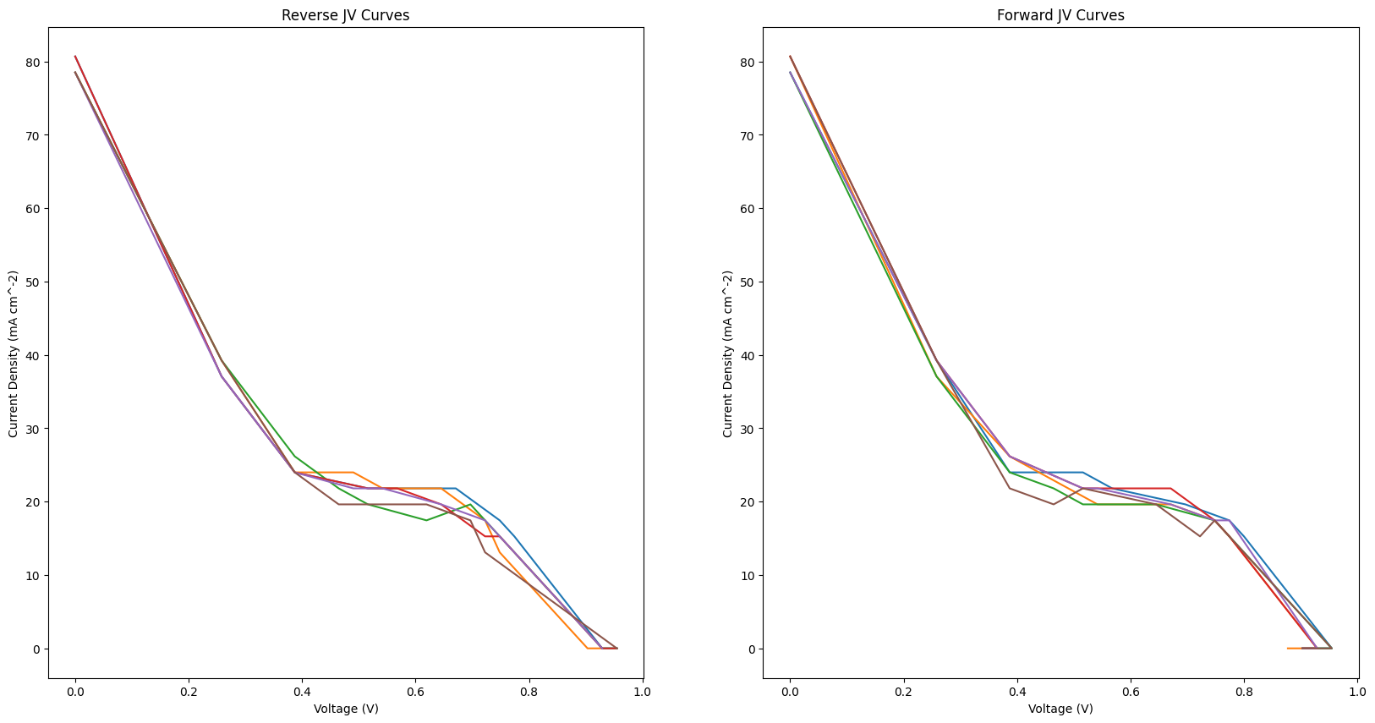
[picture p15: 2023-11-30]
Flight Payload/Perovskite Performance/P1_Assembled/X018_InSatellite/plot.png

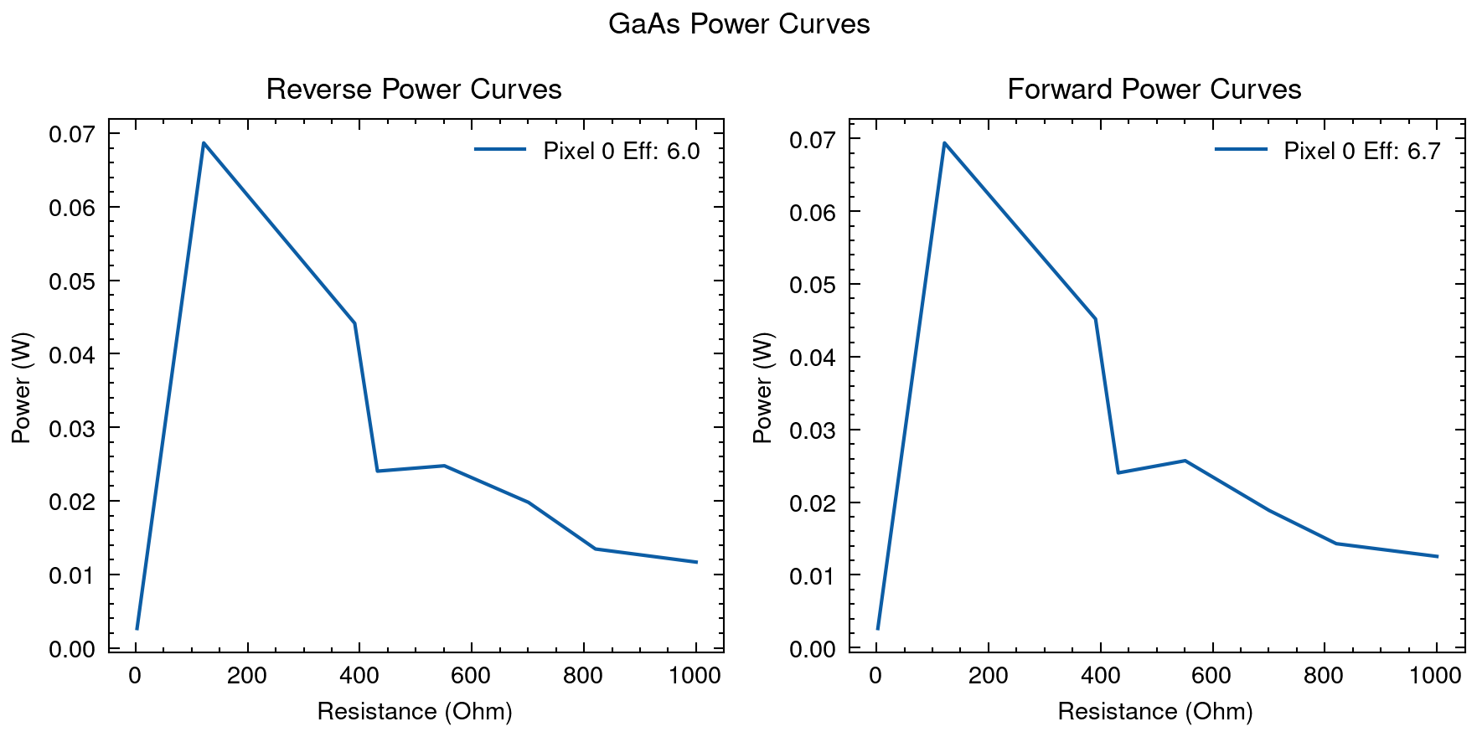
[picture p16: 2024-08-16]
Flight Payload/Perovskite Performance/GaAs_Assembled/GaAs_PreVibe/1Dec2023_power.png

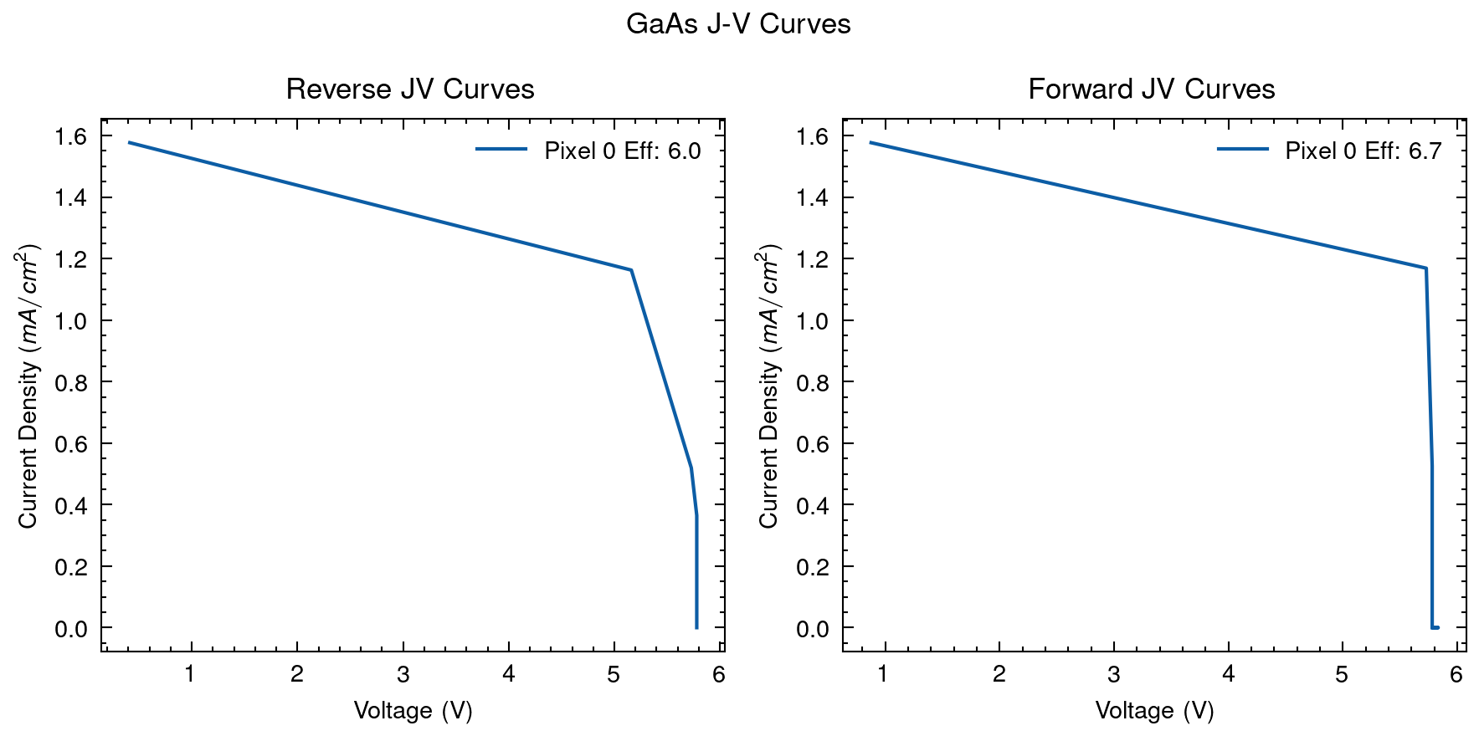
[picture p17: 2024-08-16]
Flight Payload/Perovskite Performance/GaAs_Assembled/GaAs_PreVibe/1Dec2023.png

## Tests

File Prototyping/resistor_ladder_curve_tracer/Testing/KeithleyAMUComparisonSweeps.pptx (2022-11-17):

## Temperature Dependent Measurement Data

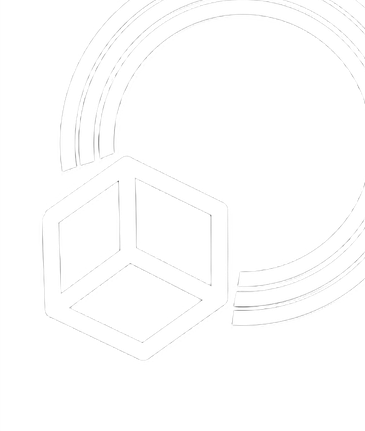
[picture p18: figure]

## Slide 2

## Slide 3

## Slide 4

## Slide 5

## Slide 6

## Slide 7

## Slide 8

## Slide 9

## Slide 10

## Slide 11

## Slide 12

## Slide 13

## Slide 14

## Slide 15

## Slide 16

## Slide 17

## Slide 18

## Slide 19

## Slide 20

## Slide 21

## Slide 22

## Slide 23

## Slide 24

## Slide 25

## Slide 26

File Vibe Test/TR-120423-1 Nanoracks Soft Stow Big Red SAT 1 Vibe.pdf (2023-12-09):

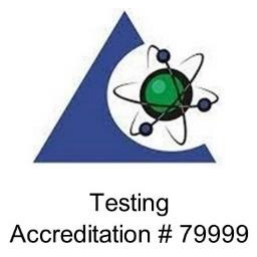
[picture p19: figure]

TR-120423-1 | Page 1

DynaQual.com / 301 Wells Fargo Dr., Houston, TX 77090

### ISO/IEC 17025:2017 ACCREDITED

## Test Report

Sine Sweep and Random Vibration

TR-120423-1 | December 04, 2023
COMPANY: | NanoRacks, LLC 503 Forge River Road Webster, TX 77598
COMPANY REP: | Maximilian Brummel, Joel Murch-Shafer
DYNAQUAL TEST TECH: | Ken Dimick
PRODUCT TESTED: | Big Red SAT 1

The undersigned have produced and reviewed the data collected and presented in the following report. By signing below, DynaQual Test Labs technical staff verifies that the data is accurate and obtained from functioning and calibrated equipment. Also, the undersigned determine that all data collection techniques are authentic, and the observations and conclusions are true results of the tests performed on the dates indicated above. This report shall not be reproduced except in full without approval of the laboratory. Lastly, the report’s results apply only to the sample(s) received for this test.

APPROVAL SIGNATURE SECTION:

Testing Performed By:

_______________________
Ken Dimick, Lab Technician

Approved By:

_______________________ | 12/06/2023
Bill Burt, Sr. Technical Writer | Date

### PROJECT SCOPE

NanoRacks, LLC requested the services of DynaQual Test Labs to perform vibration testing on one of their Soft Stow Big Red SAT assemblies. The testing consisted of sine sweep and random vibration testing.

The following test report covers the test program and describes the tests performed, with any associated input/output profiles. The testing was performed at DynaQual’s vibration lab. All equipment and sensor measurements were performed with calibrated equipment and trained, qualified personnel.

Definitions

UUT – Unit Under Test

UUT Identification

The UUT and dates the unit was subjected to testing is shown in Table 1.

Table 1 – Product Identifiers
UUT | Description | S/N | Date Tested
1 | Big Red SAT 1 | 001 | 12/04/2023

### VIBRATION TESTING PARAMETERS/SETUP

Table 2 – Description of Test Equipment
Description | Manufacturer | Model | S/N | Cal Due
Vibration System | ETS-714 Shaker | MPA714 | SH1204115 | N/A
Vibration Controller | Vibration Research | VR9500 | 9511B7F2 | 06/20/2024
Vibration Controller | Vibration Research | VR9500 | 950E43A0 | 06/20/2024
Control accelerometer | Dytran Instruments | 3055B1T | 16147 | 06/22/2024

Vibration System: ETS MPA714 15,400 lbf shaker was used to perform the testing. (Figure 1)

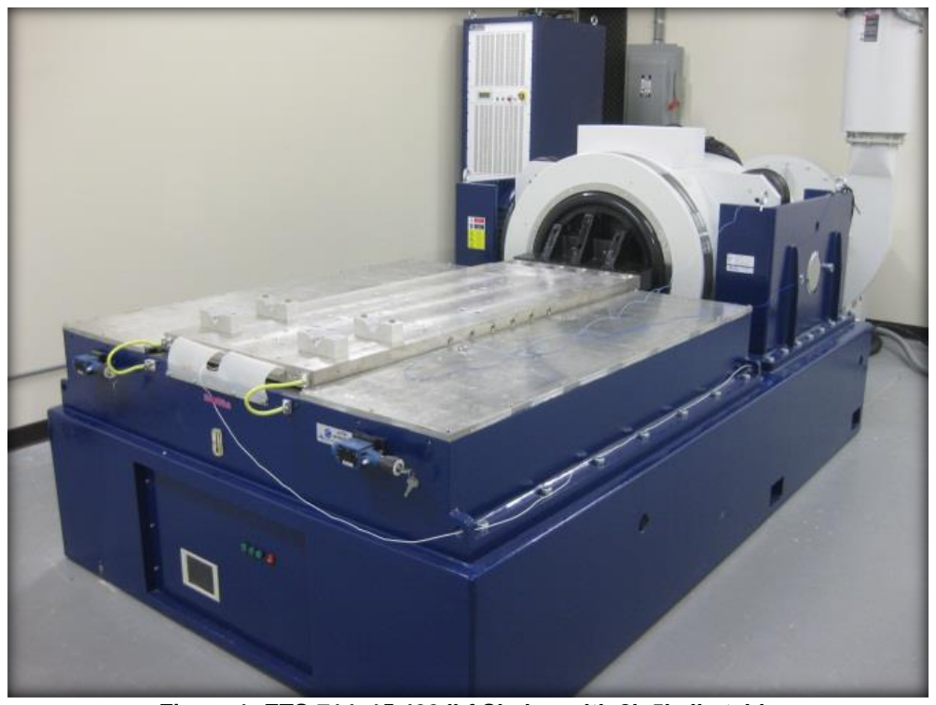
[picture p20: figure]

Figure 1: ETS-714, 15,400 lbf Shaker with 2’x5’ slip table

### Testing Program – Vibration

The UUT was subjected to testing per the following:

1. Sine sweep, 5-2000Hz, 0.5Gpeak, 2 octaves per minute, in the Z, X, and Y axes, performed both pre and post random vibration.
2. Random vibration, 20-2000Hz, 5.757Grms, for 1 minute, in the Z, X, and Y axes.

The vibration profiles are shown below in Figures 2–7.

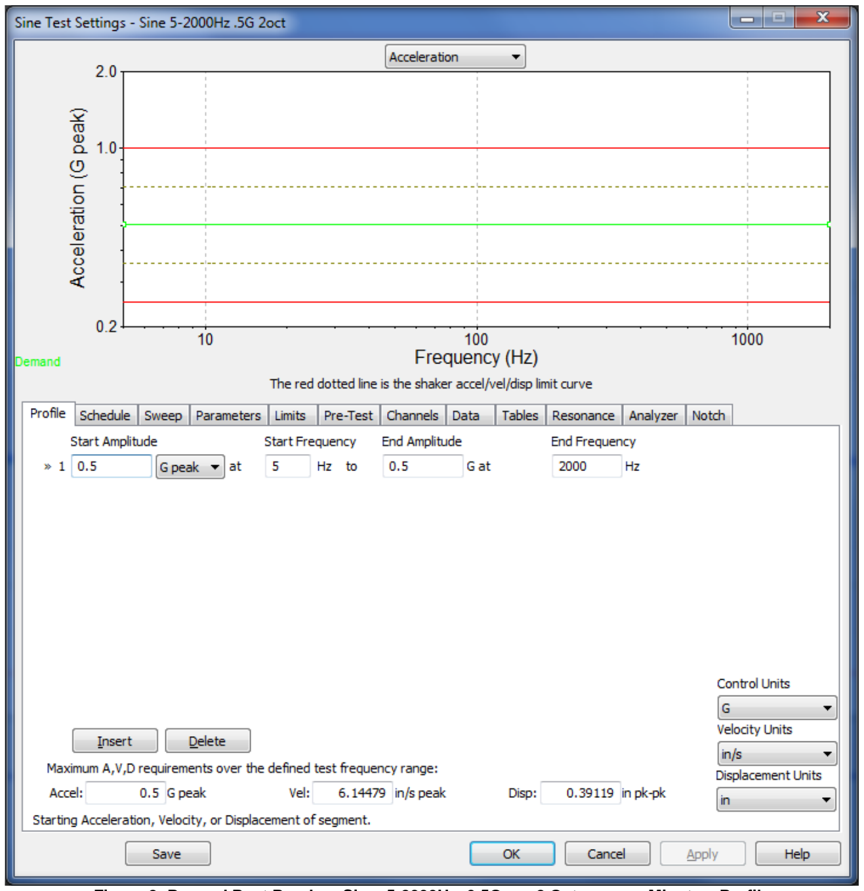
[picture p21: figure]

Figure 2: Pre and Post Random Sine, 5-2000Hz, 0.5Gpeak, 2 Octaves per Minute – Profile

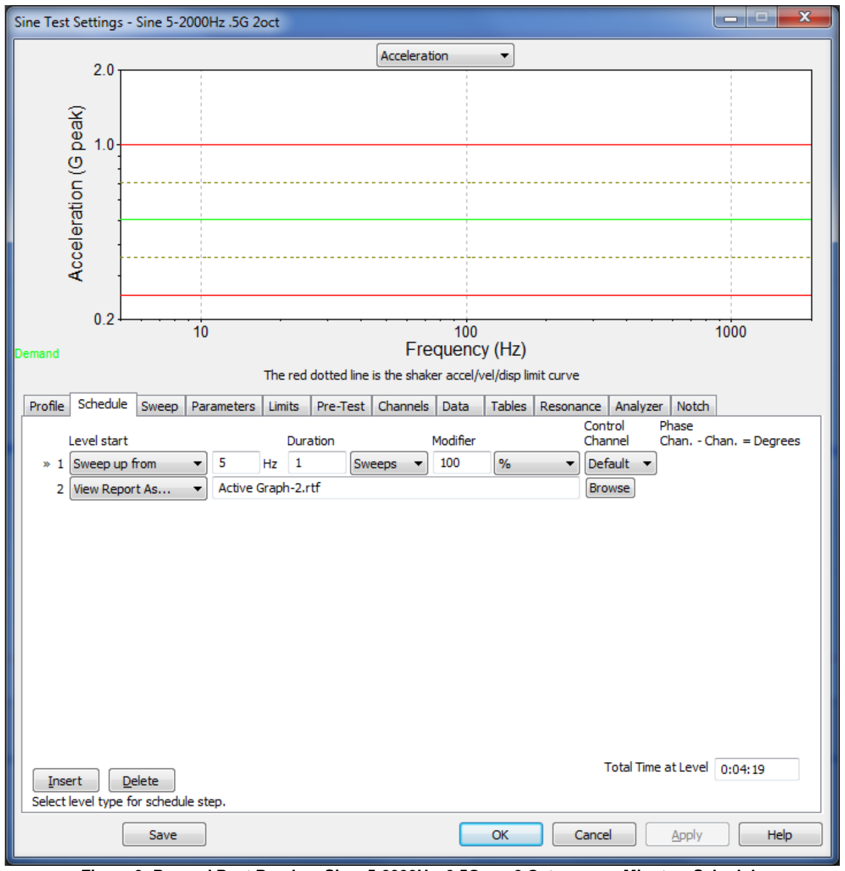
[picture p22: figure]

Figure 3: Pre and Post Random Sine, 5-2000Hz, 0.5Gpeak, 2 Octaves per Minute – Schedule

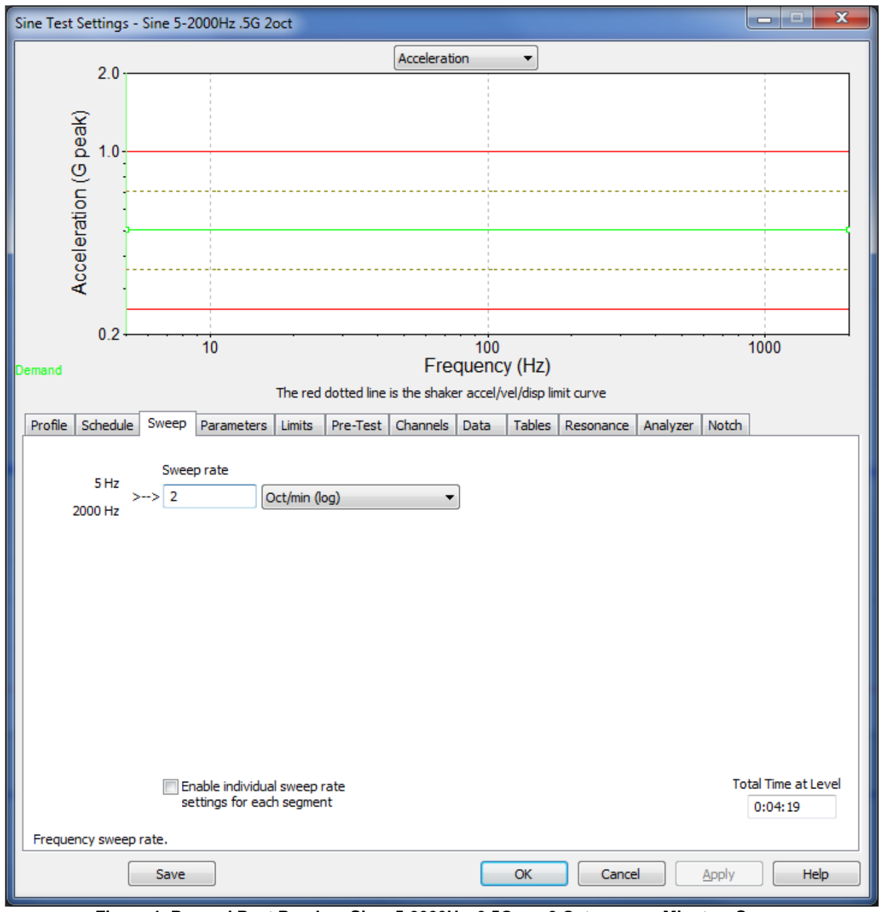
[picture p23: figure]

Figure 4: Pre and Post Random Sine, 5-2000Hz, 0.5Gpeak, 2 Octaves per Minute – Sweep

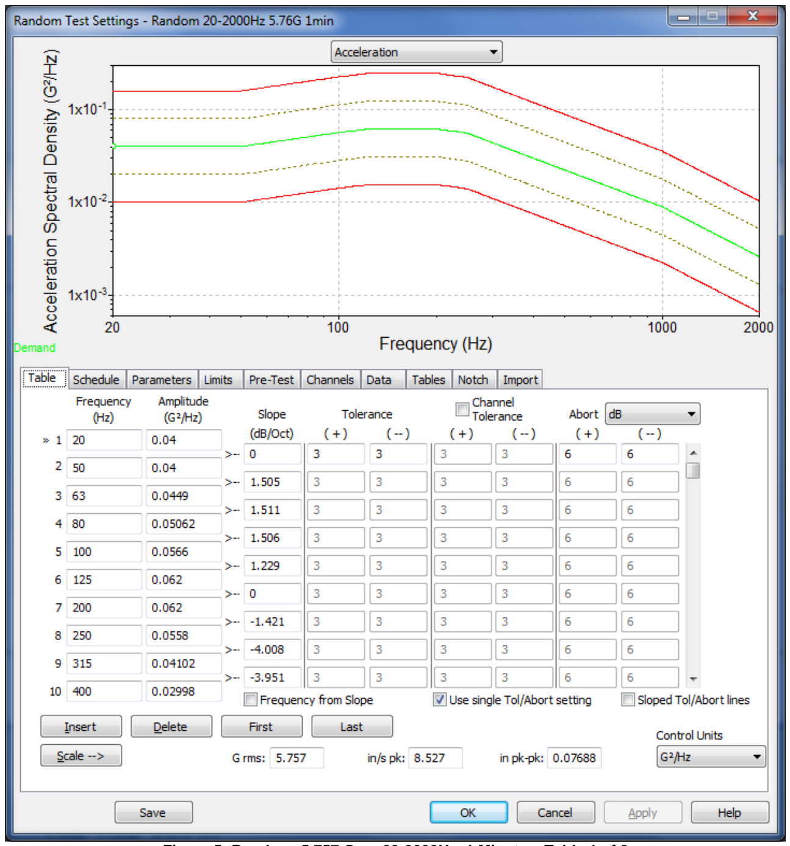
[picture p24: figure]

Figure 5: Random, 5.757 Grms, 20-2000Hz, 1 Minute – Table 1 of 2

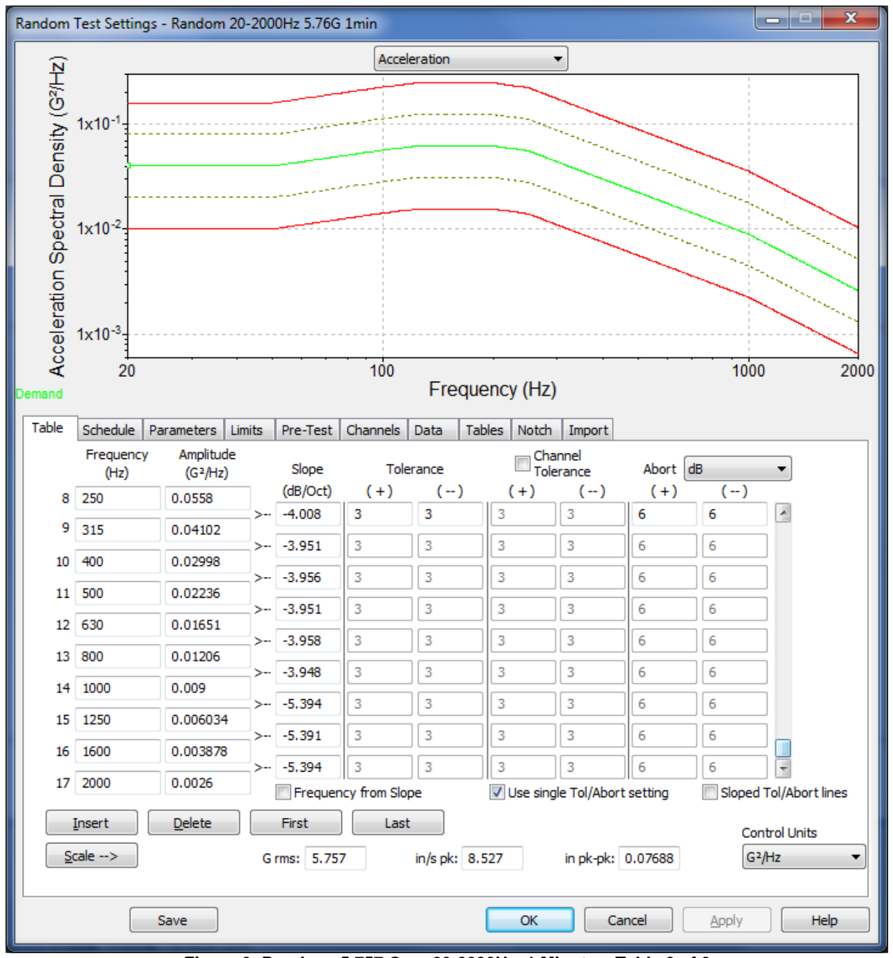
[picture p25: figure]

Figure 6: Random, 5.757 Grms, 20-2000Hz, 1 Minute – Table 2 of 2

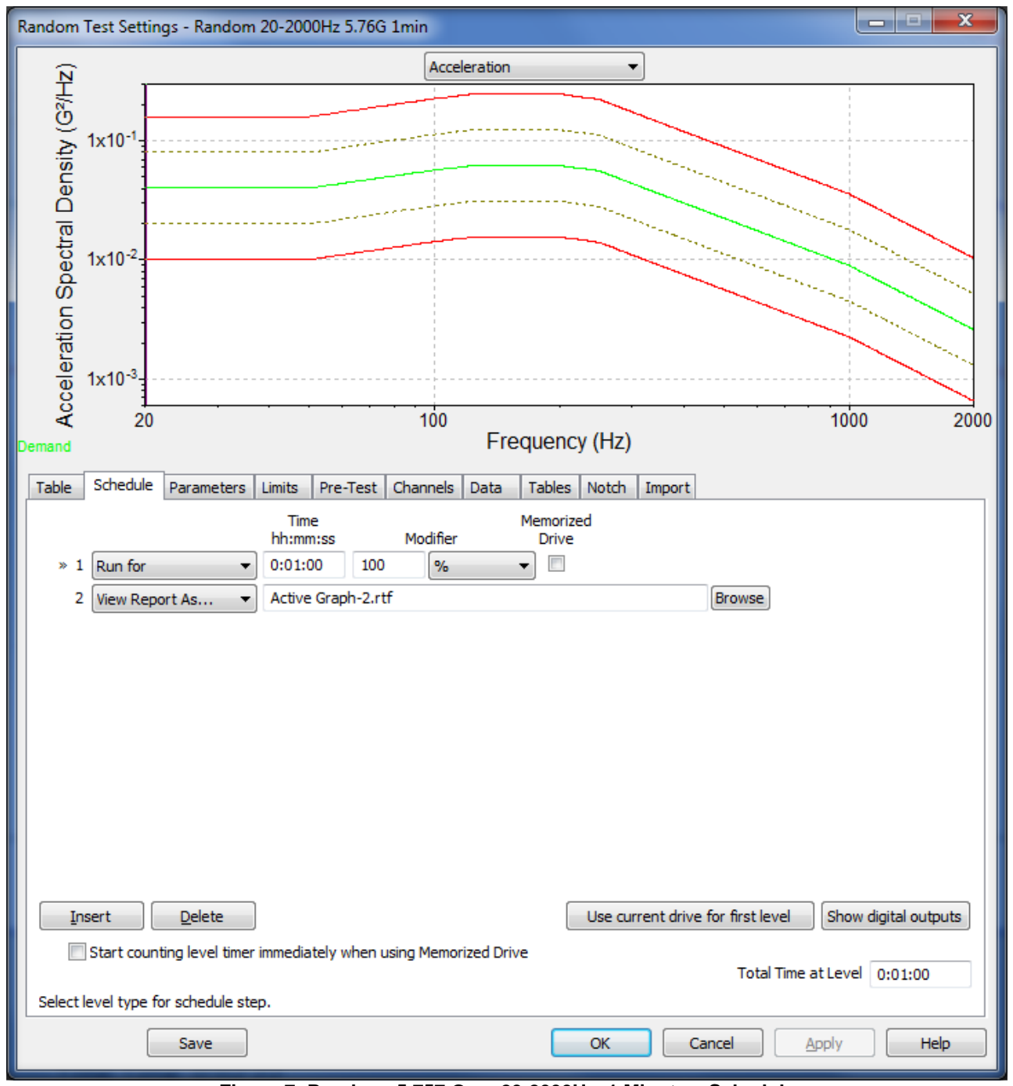
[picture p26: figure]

Figure 7: Random, 5.757 Grms, 20-2000Hz, 1 Minute – Schedule

Fixture

The UUT was secured to an aluminum extender plate. The plate and the UUT were secured to the slip table using 3 sets of 3/8-16 swivel hoist rings and straps. Testing started in the Z axis. To differentiate between the Z and X axes testing, the extender plate was rotated 90° on the slip table. For the Y axis testing, the UUT was rotated 90° horizontally on the extender plate. See Figures 8-13 below for illustrations of the UUT fixtured for testing, along with views of the control accelerometer location.

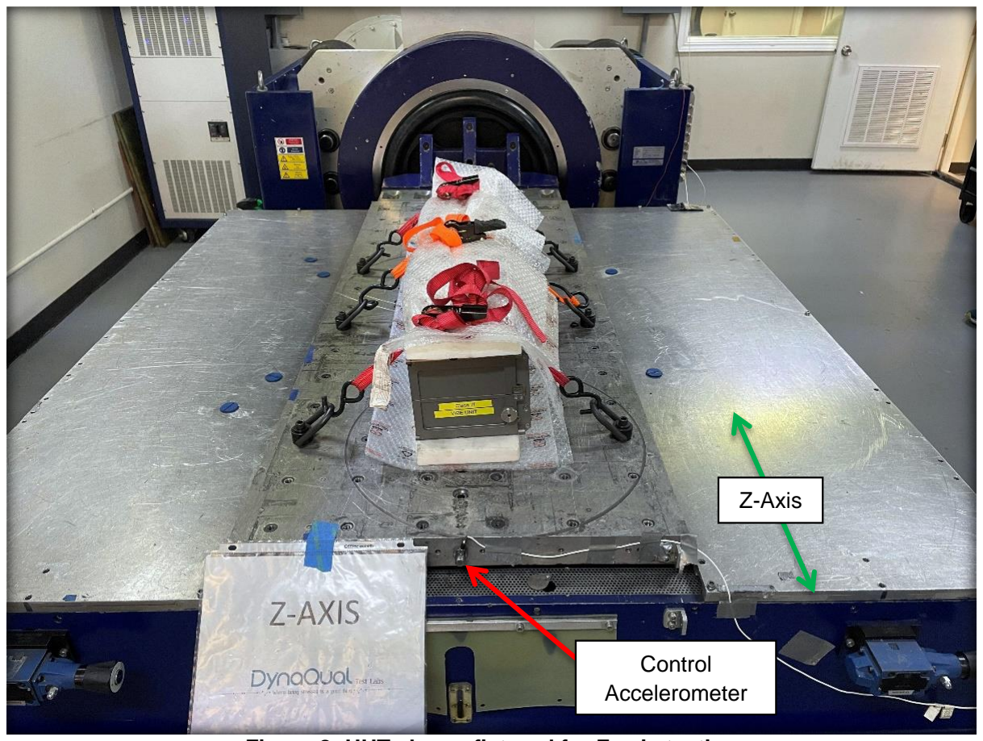
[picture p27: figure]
Control Accelerometer; Z-Axis

Figure 8: UUT shown fixtured for Z axis testing


Figure 9: Detailed view of the control accelerometer for all axes testing

Figure 10: UUT shown fixtured for X axis testing

Control
Accelerometer

Control
Accelerometer

X-Axis


Figure 12: Side view of UUT shown in X axis

Figure 11: UUT shown fixtured for Y axis testing

Figure 13 Side view of UUT shown in Y axis

Y-Axis

Control
Accelerometer

Product Functional Testing

The UUT was not powered or tested functionally during the vibration testing. The UUT was to be inspected by NanoRacks personnel at their facility upon completion of the vibration testing at DynaQual.

Vibration Testing Program

Table 3 summarizes the vibration test steps for the UUT, showing the type of test, with input parameters, any associated notes referencing the data collected, and observations or changes noted. Software generated reports for each test performed are shown below Table 3 and are also provided in the customer data file, made available after the conclusion of testing.

Table 3 – Vibration Testing Program
Test # | Axis | Test Type | Frequency | Amplitude | Duration/Rate | Notes
1 | Z | Pre Sine | 5-2000Hz | 0.5 Gpeak | 2 Oct/Min
2 | Z | Random | 20-2000Hz | 5.757 Grms | 1 Minute
3 | Z | Post Sine | 5-2000Hz | 0.5 Gpeak | 2 Oct/Min
4 | X | Pre Sine | 5-2000Hz | 0.5 Gpeak | 2 Oct/Min
5 | X | Random | 20-2000Hz | 5.757 Grms | 1 Minute
6 | X | Post Sine | 5-2000Hz | 0.5 Gpeak | 2 Oct/Min
7 | Y | Pre Sine | 5-2000Hz | 0.5 Gpeak | 2 Oct/Min
8 | Y | Random | 20-2000Hz | 5.757 Grms | 1 Minute
9 | Y | Post Sine | 5-2000Hz | 0.5 Gpeak | 2 Oct/Min | 1

Notes:

1. Testing was completed with no physical failures of the UUT observed or reported. The UUT will be inspected and functionally tested at the customer’s facility.

Test 1: Z Axis; Test Mode:; Sine (Pre-Random); Frequency:; Rate:; 2 Octaves per Minute; Amplitude:; 0.5 Gpeak; Duration; Level; 1 sweeps; Frequency (Hz); Acceleration (G peak); Acceleration Profile; Demand; Control; Dec 04, 2023 11:16:38; Demand: 0.5 G; Control: 0.5037 G; Level Time: 0:04:20; Total Time: 0:04:30; Sine 5-2000Hz .5G 2oct; Z-Axis

Data: C:\VibrationVIEW\Data\2023-12\2023Dec04-1112-0001.vsd
Test: C:\VibrationVIEW\Profiles\Customers Profiles\Customer Profiles\NanoRacks\Sine 5-2000Hz .5G 2oct.vsp
Data stored on Dec 04, 2023 11:16:38

Soft Stow: Big Red SAT 1

Test level schedule:

2) View Report (prompt)
** Test started Dec 04, 2023 11:12:09, running for 0:04:30
** Current level: 1, running at 100 % for 0:04:20 of 1 sweeps

Test 2: Z Axis; Test Mode:; Random; Frequency:; Duration:; 1 Minute; Amplitude:; 5.757 Grms; Duration; Level; Frequency (Hz); Demand; Control; Dec 04, 2023 11:20:59; Demand: 5.757 G RMS; Control: 5.757 G RMS; Level 1) 100 %; Level Time: 0:01:00; Total Time: 0:02:12; Random 20-2000Hz 5.76G 1min; Z-Axis

Data: C:\VibrationVIEW\Data\2023-12\2023Dec04-1118-0001.vrd
Test: C:\VibrationVIEW\Profiles\Customers Profiles\Customer Profiles\NanoRacks\Random 20-2000Hz 5.76G
1min.vrp
Data stored on Dec 04, 2023 11:20:59

Acceleration Spectral Density

Acceleration Spectral Density (G²/Hz)

Soft Stow: Big Red SAT 1

Test level schedule:

2) View Report (prompt)
** Test started Dec 04, 2023 11:18:47, running for 0:02:12
** Current level: 1, running at 100 % for 0:01:00 of 0:01:00

Test 3: Z Axis; Test Mode:; Sine (Post-Random); Frequency:; Rate:; 2 Octaves per Minute; Amplitude:; 0.5 Gpeak; Duration; Level; 1 sweeps; Frequency (Hz); Acceleration (G peak); Acceleration Profile; Demand; Control; Dec 04, 2023 11:26:29; Demand: 0.5 G; Control: 0.4975 G; Level Time: 0:04:20; Total Time: 0:04:29; Sine 5-2000Hz .5G 2oct

Data: C:\VibrationVIEW\Data\2023-12\2023Dec04-1122-0001.vsd
Test: C:\VibrationVIEW\Profiles\Customers Profiles\Customer Profiles\NanoRacks\Sine 5-2000Hz .5G 2oct.vsp
Data stored on Dec 04, 2023 11:26:29

Soft Stow: Big Red SAT 1

Post-Sine: Z-Axis

Test level schedule:

2) View Report (prompt)
** Test started Dec 04, 2023 11:22:00, running for 0:04:29
** Current level: 1, running at 100 % for 0:04:20 of 1 sweeps

Test 4: X Axis; Test Mode:; Sine (Pre-Random); Frequency:; Rate:; 2 Octaves per Minute; Amplitude:; 0.5 Gpeak; Duration; Level; 1 sweeps; Frequency (Hz); Acceleration (G peak); Acceleration Profile; Demand; Control; Dec 04, 2023 11:55:24; Demand: 0.5 G; Control: 0.5041 G; Level Time: 0:04:20; Total Time: 0:04:29; Sine 5-2000Hz .5G 2oct

Data: C:\VibrationVIEW\Data\2023-12\2023Dec04-1150-0001.vsd
Test: C:\VibrationVIEW\Profiles\Customers Profiles\Customer Profiles\NanoRacks\Sine 5-2000Hz .5G 2oct.vsp
Data stored on Dec 04, 2023 11:55:24

Soft Stow: Big Red SAT 1

Pre-Sine: X-Axis

Test level schedule:

2) View Report (prompt)
** Test started Dec 04, 2023 11:50:55, running for 0:04:29
** Current level: 1, running at 100 % for 0:04:20 of 1 sweeps

Test 5: X Axis; Test Mode:; Random; Frequency:; Duration:; 1 Minute; Amplitude:; 5.757 Grms; Duration; Level; Frequency (Hz); Demand; Control; Dec 04, 2023 11:58:16; Demand: 5.757 G RMS; Control: 5.757 G RMS; Level 1) 100 %; Level Time: 0:01:00; Total Time: 0:02:17; Random 20-2000Hz 5.76G 1min; X-Axis

Data: C:\VibrationVIEW\Data\2023-12\2023Dec04-1156-0001.vrd
Test: C:\VibrationVIEW\Profiles\Customers Profiles\Customer Profiles\NanoRacks\Random 20-2000Hz 5.76G
1min.vrp
Data stored on Dec 04, 2023 11:58:16

Acceleration Spectral Density

Acceleration Spectral Density (G²/Hz)

Soft Stow: Big Red SAT 1

Test level schedule:

2) View Report (prompt)
** Test started Dec 04, 2023 11:56:00, running for 0:02:17
** Current level: 1, running at 100 % for 0:01:00 of 0:01:00

Test 6: X Axis; Test Mode:; Sine (Post-Random); Frequency:; Rate:; 2 Octaves per Minute; Amplitude:; 0.5 Gpeak; Duration; Level; 1 sweeps; Frequency (Hz); Acceleration (G peak); Acceleration Profile; Demand; Control; Dec 04, 2023 12:03:24; Demand: 0.5 G; Control: 0.4997 G; Level Time: 0:04:20; Total Time: 0:04:29; Sine 5-2000Hz .5G 2oct

Data: C:\VibrationVIEW\Data\2023-12\2023Dec04-1158-0001.vsd
Test: C:\VibrationVIEW\Profiles\Customers Profiles\Customer Profiles\NanoRacks\Sine 5-2000Hz .5G 2oct.vsp
Data stored on Dec 04, 2023 12:03:24

Soft Stow: Big Red SAT 1

Post-Sine: X-Axis

Test level schedule:

2) View Report (prompt)
** Test started Dec 04, 2023 11:58:55, running for 0:04:29
** Current level: 1, running at 100 % for 0:04:20 of 1 sweeps

Test 7: Y Axis; Test Mode:; Sine (Pre-Random); Frequency:; Rate:; 2 Octaves per Minute; Amplitude:; 0.5 Gpeak; Duration; Level; 1 sweeps; Frequency (Hz); Acceleration (G peak); Acceleration Profile; Demand; Control; Dec 04, 2023 12:15:57; Demand: 0.5 G; Control: 0.492 G; Level Time: 0:04:20; Total Time: 0:04:29; Sine 5-2000Hz .5G 2oct

Data: C:\VibrationVIEW\Data\2023-12\2023Dec04-1211-0001.vsd
Test: C:\VibrationVIEW\Profiles\Customers Profiles\Customer Profiles\NanoRacks\Sine 5-2000Hz .5G 2oct.vsp
Data stored on Dec 04, 2023 12:15:57

Soft Stow: Big Red SAT 1

Pre-Sine: Y-Axis

Test level schedule:

2) View Report (prompt)
** Test started Dec 04, 2023 12:11:28, running for 0:04:29
** Current level: 1, running at 100 % for 0:04:20 of 1 sweeps

Test 8: Y Axis; Test Mode:; Random; Frequency:; Duration:; 1 Minute; Amplitude:; 5.757 Grms; Duration; Level; Frequency (Hz); Demand; Control; Dec 04, 2023 12:18:55; Demand: 5.757 G RMS; Control: 5.757 G RMS; Level 1) 100 %; Level Time: 0:01:00; Total Time: 0:02:22; Random 20-2000Hz 5.76G 1min; Y-Axis

Data: C:\VibrationVIEW\Data\2023-12\2023Dec04-1216-0001.vrd
Test: C:\VibrationVIEW\Profiles\Customers Profiles\Customer Profiles\NanoRacks\Random 20-2000Hz 5.76G
1min.vrp
Data stored on Dec 04, 2023 12:18:55

Acceleration Spectral Density

Acceleration Spectral Density (G²/Hz)

Soft Stow: Big Red SAT 1

Test level schedule:

2) View Report (prompt)
** Test started Dec 04, 2023 12:16:33, running for 0:02:22
** Current level: 1, running at 100 % for 0:01:00 of 0:01:00

Test 9: Y Axis; Test Mode:; Sine (Post-Random); Frequency:; Rate:; 2 Octaves per Minute; Amplitude:; 0.5 Gpeak; Duration; Level; 1 sweeps; Frequency (Hz); Acceleration (G peak); Acceleration Profile; Demand; Control; Dec 04, 2023 12:24:13; Demand: 0.5 G; Control: 0.4974 G; Level Time: 0:04:20; Total Time: 0:04:29; Sine 5-2000Hz .5G 2oct

Data: C:\VibrationVIEW\Data\2023-12\2023Dec04-1219-0001.vsd
Test: C:\VibrationVIEW\Profiles\Customers Profiles\Customer Profiles\NanoRacks\Sine 5-2000Hz .5G 2oct.vsp
Data stored on Dec 04, 2023 12:24:13

Soft Stow: Big Red SAT 1

Post-Sine: Y-Axis

Test level schedule:

2) View Report (prompt)
** Test started Dec 04, 2023 12:19:44, running for 0:04:29
** Current level: 1, running at 100 % for 0:04:20 of 1 sweeps

### TESTING SUMMARY/CONCLUSIONS

The following summarizes the vibration testing performed for NanoRacks, LLC on one Soft Stow Big Red SAT 1 assembly, on December 4, 2023.

1. DynaQual test labs performed vibration one Big Red SAT assembly for NanoRacks on 12/04/2023.
2. Pre, and Post Random Sine Sweeps were performed at 0.5 Gpeak, from 5-2000Hz, at a rate of 2 octaves per minute, in the Z, X, and Y axes.
3. Random Vibration was done between the frequencies of 20-2000Hz, at a level of 5.757 Grms, for a period of 1 minute in the Z, X and Y axes.
4. The UUT was not powered during testing but was returned to NanoRacks LLC for inspection and functional testing after the vibration testing concluded.
5. No visible or mechanical failures were observed or reported by NanoRacks personnel during the testing.
6. The testing provided quality data for further analysis by NanoRacks, LLC personnel back at their facility.

Data File Provided to Customer (Profile Screen Shots, Graphs, Test Data, Pictures of set up)

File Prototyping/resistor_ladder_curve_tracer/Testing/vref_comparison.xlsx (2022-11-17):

 | Measured Voltage | Actual Voltage | Difference
AVCC Ref | 0.461 | 0.505 | 0.0442
 | 0.913 | 1.000 | 0.0872
 | 1.283 | 1.405 | 0.1216 | `
2V5 Ref | 0.510 | 0.509 | -0.0006
 | 1.004 | 1.001 | -0.0030
 | 1.345 | 1.341 | -0.0036

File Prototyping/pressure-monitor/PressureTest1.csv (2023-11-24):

 | Pressure | Temperature | Timestamp
0 | 1020.354919 | 42.86000061 | 32:53.4
1 | 1020.365295 | 42.86000061 | 32:54.5
2 | 1020.354858 | 42.84999847 | 32:55.6
3 | 1020.317566 | 42.84999847 | 32:56.6
4 | 1020.314453 | 42.84999847 | 32:57.6
5 | 1020.312683 | 42.84999847 | 32:58.7
6 | 1020.311462 | 42.84000015 | 32:59.7
7 | 1020.317322 | 42.84999847 | 33:00.7
8 | 1020.283508 | 42.84000015 | 33:01.8
9 | 1020.283386 | 42.84000015 | 33:02.8
10 | 1020.269043 | 42.84000015 | 33:03.8
11 | 1020.26593 | 42.84000015 | 33:04.9
12 | 1020.255005 | 42.83000183 | 33:06.0
13 | 1020.281433 | 42.84000015 | 33:07.0
14 | 1020.284912 | 42.84000015 | 33:08.1
15 | 1020.263672 | 42.84000015 | 33:09.3
16 | 1020.245789 | 42.83000183 | 33:10.4
17 | 1020.224548 | 42.83000183 | 33:11.5
18 | 1020.247559 | 42.83000183 | 33:12.5
19 | 1020.206177 | 42.81999969 | 33:13.6
20 | 1020.226501 | 42.83000183 | 33:14.7
21 | 1020.205139 | 42.83000183 | 33:15.7
22 | 1020.203308 | 42.81999969 | 33:16.7
23 | 1020.176147 | 42.81000137 | 33:17.8
24 | 1020.199768 | 42.81999969 | 33:18.8
25 | 1020.183289 | 42.81000137 | 33:19.8
26 | 1020.154541 | 42.81000137 | 33:20.9
27 | 1020.16687 | 42.81000137 | 33:21.9
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

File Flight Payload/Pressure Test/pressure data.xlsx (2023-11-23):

 | Pressure |  | Humidity
98688 | 986.88 | 2019 | 20.19 | 0.1 | 0.001666666667
98680 | 986.8 | 2020 | 20.2 | 0.2 | 0.003333333333
98685 | 986.85 | 2020 | 20.2 | 0.3 | 0.005
98688 | 986.88 | 2017 | 20.17 | 0.4 | 0.006666666667
98683 | 986.83 | 2019 | 20.19 | 0.5 | 0.008333333333
98683 | 986.83 | 2019 | 20.19 | 0.6 | 0.01
98688 | 986.88 | 2020 | 20.2 | 0.7 | 0.01166666667
98683 | 986.83 | 2019 | 20.19 | 0.8 | 0.01333333333
98680 | 986.8 | 2019 | 20.19 | 0.9 | 0.015
98683 | 986.83 | 2018 | 20.18 | 1 | 0.01666666667
98685 | 986.85 | 2020 | 20.2 | 1.1 | 0.01833333333
98685 | 986.85 | 2019 | 20.19 | 1.2 | 0.02
98688 | 986.88 | 2020 | 20.2 | 1.3 | 0.02166666667
98688 | 986.88 | 2018 | 20.18 | 1.4 | 0.02333333333
98685 | 986.85 | 2019 | 20.19 | 1.5 | 0.025
98685 | 986.85 | 2019 | 20.19 | 1.6 | 0.02666666667
98683 | 986.83 | 2019 | 20.19 | 1.7 | 0.02833333333
98685 | 986.85 | 2016 | 20.16 | 1.8 | 0.03
98685 | 986.85 | 2019 | 20.19 | 1.9 | 0.03166666667
98688 | 986.88 | 2020 | 20.2 | 2 | 0.03333333333
98683 | 986.83 | 2020 | 20.2 | 2.1 | 0.035
98685 | 986.85 | 2019 | 20.19 | 2.2 | 0.03666666667
98685 | 986.85 | 2019 | 20.19 | 2.3 | 0.03833333333
98688 | 986.88 | 2022 | 20.22 | 2.4 | 0.04
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

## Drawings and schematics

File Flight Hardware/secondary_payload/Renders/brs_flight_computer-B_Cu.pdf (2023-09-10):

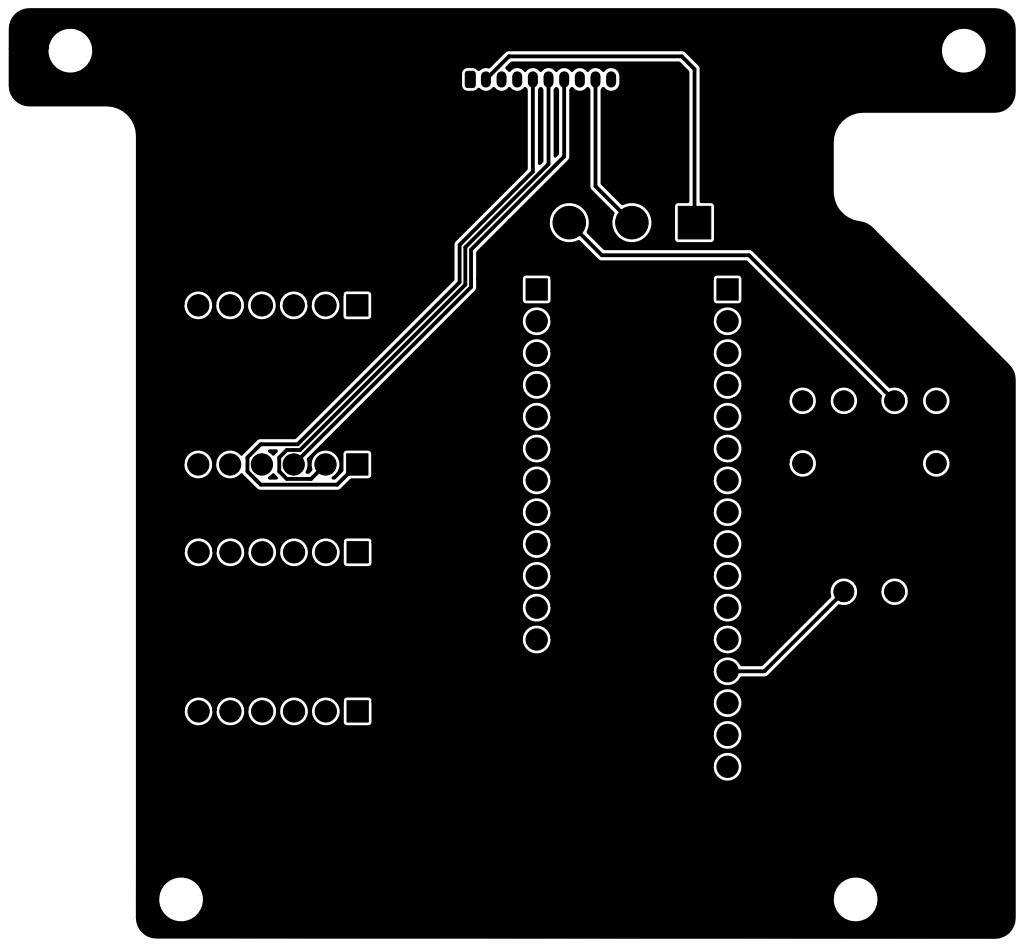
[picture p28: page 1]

Approved: WSA
Designer: WSA Reviewer: WSA

Copyright (c) 2023
File: brs_flight_computer.kicad_pcb Sheet: UNL Aerospace Club | Advanced eXperimental Payloads

Id: 1/1 Title: Big Red Satellite Secondary Payload - Layout

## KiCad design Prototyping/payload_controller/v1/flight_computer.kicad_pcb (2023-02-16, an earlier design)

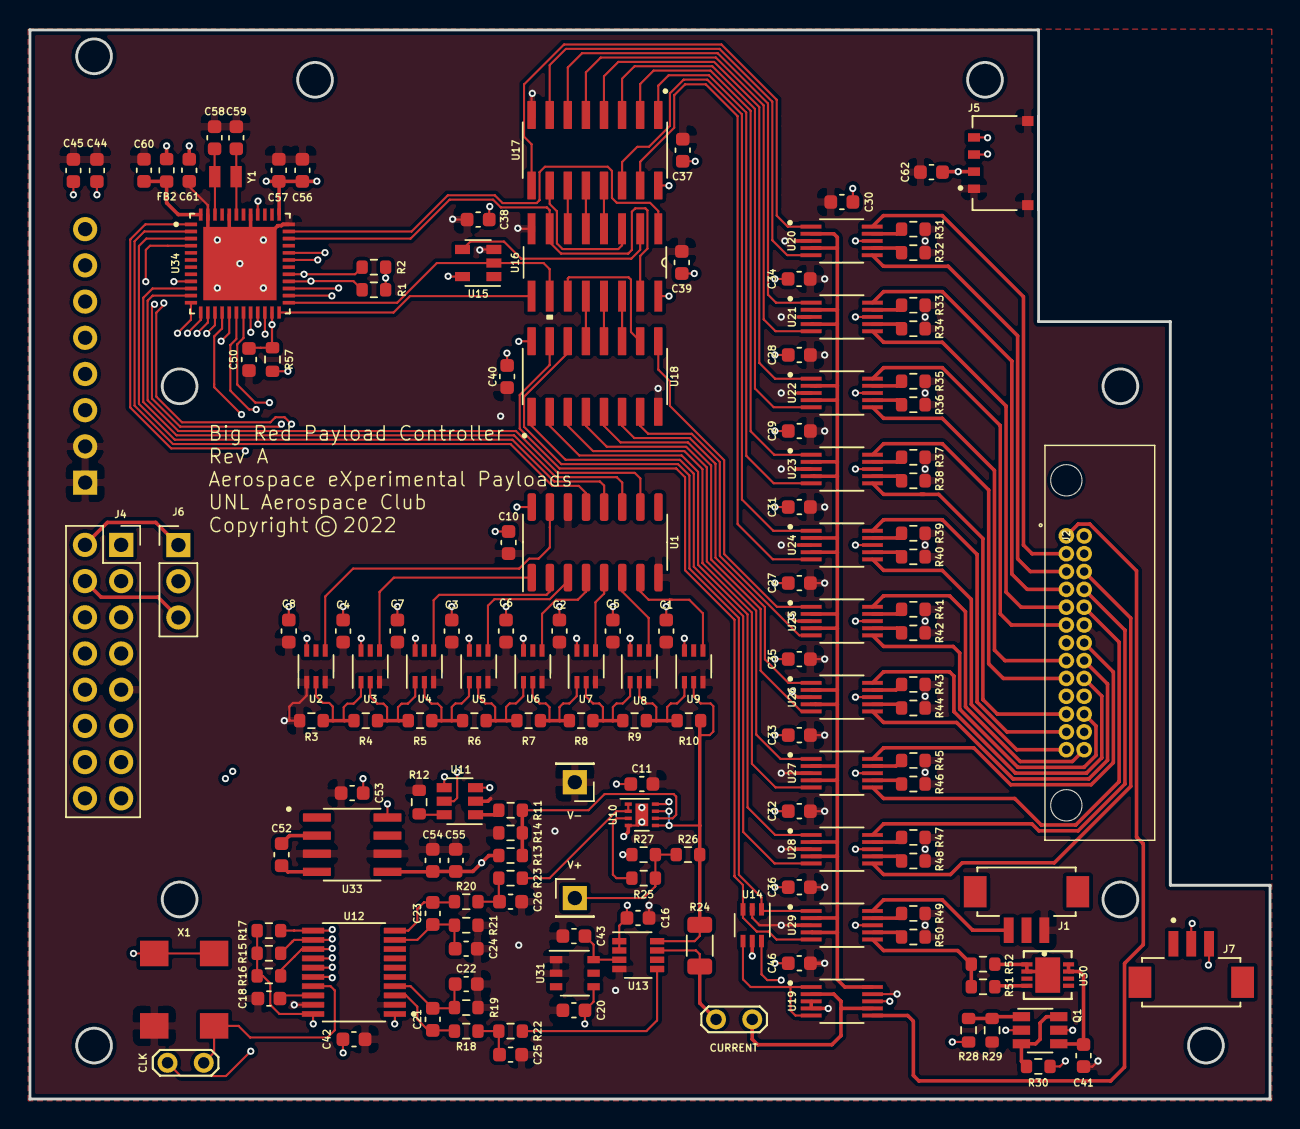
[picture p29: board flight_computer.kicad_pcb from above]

Board: 4 copper layers, 87.0 x 75.0 mm, 152 parts (1 on the bottom side), 151 nets.

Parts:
C1, C2, C3, C4, C5, C6, C7, C8, C10, C11, C16, C27, C28, C29, C30, C31, C32, C33, C34, C35, C36, C37, C38, C39, C40, C41, C42, C45, C46, C50, C53, C54, C56, C60, C61, C62: 0.1u; C_0603_1608Metric
C18: 220n; C_0603_1608Metric
C20, C43, C57: 1u; C_0603_1608Metric
C21, C22, C23, C24: 10n; C_0603_1608Metric
C25, C26, C44, C52: 10u; C_0603_1608Metric
C55: CP; C_0603_1608Metric
C58, C59: 10p; C_0603_1608Metric
CLK: ADC_CLK Connect; TestPoint_2Pads_Pitch2.54mm_Drill0.8mm
CURRENT: Current Test; TestPoint_2Pads_Pitch2.54mm_Drill0.8mm
FB2: Ferrite_Bead_Small; L_0603_1608Metric
J1: GaAs Cell; HRS_DF13C-3P-1.25V(21)
J2: G125-MH12605M4R
J3: Conn_01x08_Female; PinSocket_1x08_P2.54mm_Vertical
J4: Conn_02x07_Odd_Even; PinSocket_2x08_P2.54mm_Vertical
J5: 0781710004; MOLEX_0781710004
J6: Conn_01x03_Male; PinHeader_1x03_P2.54mm_Vertical
J7: GaAs Temp; HRS_DF13C-3P-1.25V(21)
Q1: DMC2053UVT; TSOT-23-6
R1, R2: 4.7k; R_0603_1608Metric
R3: 50; R_0603_1608Metric
R4: 250; R_0603_1608Metric
R5: 500; R_0603_1608Metric
R6: 1000; R_0603_1608Metric
R7: 2000; R_0603_1608Metric
R8: 4000; R_0603_1608Metric
R9: 8000; R_0603_1608Metric
R10: 16000; R_0603_1608Metric
R11, R14: 100k; R_0603_1608Metric
R12, R28: 1k; R_0603_1608Metric
R13: 500k; R_0603_1608Metric
R15, R16, R17, R22, R23, R29, R30: 10k; R_0603_1608Metric
R18, R19, R20, R21, R25: 470; R_0603_1608Metric
R24: 510m; R_1206_3216Metric
R26, R27: 10M; R_0603_1608Metric
R31, R32, R33, R34, R35, R36, R37, R38, R39, R40, R41, R42, R43, R44, R45, R46, R47, R48, R49, R50, R57: R; R_0603_1608Metric
R51: 20k; R_0603_1608Metric
R52: 1; R_0603_1608Metric
U1: 74HC590; SOIC-16_3.9x9.9mm_P1.27mm
U2, U3, U4, U5, U6, U7, U8, U9: ADG841YKSZ-500RL7
U10: OPA2387; WSON-8-1EP_2x2mm_P0.5mm_EP0.9x1.6mm
U11: MCP4725xxx-xCH; SOT-23-6
U12: ADS131M04IPWR; SOP65P640X120-20N
U13: INA190A4IDDFR
U14: 74LVC1G332; ADG841YKSZ-500RL7
U15: SN74LVC1G14DRL; SOT-23-5
U16: CD4518BM96
U17, U18: CD4028BMT; SOIC127P600X175-16N
U19, U20, U21, U22, U23, U24, U25, U26, U27, U28, U29: MAX4736EUBT; SOP50P490X110-10N
U30: LT3092EDD#TRPBF; DFN-8_DD
U31: LT6654AMPS6-1.25; LT6654AMPS6-1.25-TRMPBF
U33: ICL7660CSAT; SOIC127P600X175-8N
U34: MSP430FR5969IRGZR; QFN50P700X700X100-49N
V+: Voltage Test+; PinHeader_1x01_P2.54mm_Vertical
V-: Voltage Test-; PinHeader_1x01_P2.54mm_Vertical
X1: CB3LV-3I-8M1920; OSCCC700X500X180-4N
Y1: CM8V-T1A; XTAL_CM8V-T1A-32.768KHZ-7PF-20PPM-TA-QC

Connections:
+3V3: C1.1, C2.1, C3.1, C4.1, C5.1, C6.1, C7.1, C8.1, C10.1, C11.1, C16.1, C20.1, C27.1, C28.1, C29.1, C30.1, C31.1, C32.1, C33.1, C34.1, C35.1, C36.1, C37.1, C38.1, C39.1, C40.1, C42.1, C44.1, C45.2, C46.1, C53.2, C56.1, C57.1, C61.1, C62.2, FB2.1, J2.14, J3.7, J3.8, J5.2, J6.2, J7.2, Q1.2, R1.2, R2.2, R15.1, R16.1, R17.1, R30.1, R57.2, U1.16, U2.6, U3.6, U4.6, U5.6, U6.6, U7.6, U8.6, U9.6, U10.8, U11.3, U12.1, U12.20, U13.1, U13.2, U14.5, U15.5, U16.16, U17.16, U18.16, U19.8, U20.8, U21.8, U22.8, U23.8, U24.8, U25.8, U26.8, U27.8, U28.8, U29.8, U31.4, U33.8, U34.37, X1.1, X1.4
-3V3: C54.2, C55.2, R13.2, U10.4, U10.9, U33.5
/Curve Tracer/ADC_CLK: CLK.1, U34.19
/Curve Tracer/ADC_CS: R15.2, U12.12, U34.9
/Curve Tracer/ADC_DRDY: R16.2, U12.13, U34.4
/Curve Tracer/ADC_SYNC: R17.2, U12.11, U34.40
/Curve Tracer/LADDER_VOLTAGE: R10.1, R24.1, R26.2, U9.2, U10.5, U10.7, U13.8
/Curve Tracer/MISO: U12.15, U34.32
/Curve Tracer/MOSI: U12.16, U34.31
/Curve Tracer/SCLK: U12.14, U34.26
/Payload Controller/0-9_CLOCK: U16.1, U34.35
/Payload Controller/10-19_CLOCK: U16.9, U34.24
/Payload Controller/ALERT: J2.7, J2.10, J2.25, U34.16
/Payload Controller/ENABLE_PANEL_SWITCH: U15.2, U16.10, U34.25
/Payload Controller/ENABLE_TEST_SOURCE: R28.2, U34.18
/Payload Controller/GAAS_TEMP: J7.3, U34.17
/Payload Controller/LADDER_CLOCK: U1.11, U34.10
/Payload Controller/LADDER_LATCH: U1.13, U34.2
/Payload Controller/RESET_PANEL_SWITCH: U16.7, U16.15, U34.34
/Payload Controller/REVERSE_BIAS: U14.6, U34.1
/Payload Controller/SCL: J2.23, J5.3, R1.1, U11.5, U34.28
/Payload Controller/SDA: J2.15, J5.4, R2.1, U11.4, U34.29
/Payload Controller/~LADDER_EN: U1.12, U34.3
/Payload Controller/~LADDER_RESET: U1.10, U34.11
/Perovskite Switches/PANEL_POSITIVE: CURRENT.1, U19.2, U19.7
FAULT: J3.6, U34.27
GND: C1.2, C2.2, C3.2, C4.2, C5.2, C6.2, C7.2, C8.2, C10.2, C11.2, C16.2, C18.2, C20.2, C22.2, C24.2, C25.2, C26.2, C27.2, C28.2, C29.2, C30.2, C31.2, C32.2, C33.2, C34.2, C35.2, C36.2, C37.2, C38.2, C39.2, C40.2, C41.1, C42.2, C43.2, C44.2, C45.1, C46.2, C50.1, C53.1, C54.1, C55.1, C56.2, C57.2, C58.1, C59.1, C60.2, C61.2, C62.1, J1.1, J2.19, J3.1, J3.2, J4.9, J5.1, J5.S1, J5.S2, Q1.5, R3.2, R12.1, R14.2, R19.2, R21.2, R27.1, R29.2, R31.1, R32.1, R33.1, R34.1, R35.1, R36.1, R37.1, R38.1, R39.1, R40.1, R41.1, R42.1, R43.1, R44.1, R45.1, R46.1, R47.1, R48.1, R49.1, R50.1, U1.8, U1.14, U2.1, U2.3, U3.3, U4.3, U5.3, U6.3, U7.3, U8.3, U9.3, U11.2, U12.2, U12.19, U13.4, U14.2, U15.3, U16.8, U17.8, U18.8, U19.3, U19.4, U19.9, U20.3, U21.3, U22.3, U23.3, U24.3, U25.3, U26.3, U27.3, U28.3, U29.3, U31.1, U31.2, U33.3, U33.6, U34.36, U34.41, U34.44, U34.47, U34.49, V-.1, X1.2
unnamed: C18.1, U12.18
unnamed: C21.1, R18.1, U12.3
unnamed: C21.2, C22.1, R19.1, U12.4
unnamed: C23.1, R20.1, U12.10
unnamed: C23.2, C24.1, R21.1, U12.9
unnamed: C25.1, R18.2, R22.1
unnamed: C26.1, R20.2, R23.1
unnamed: C41.2, Q1.4, U30.7, U30.8
unnamed: C43.1, U13.3, U31.6
unnamed: C52.1, U33.2
unnamed: C52.2, U33.4
unnamed: C58.2, U34.46, Y1.1
unnamed: C59.2, U34.43, Y1.2
unnamed: C60.1, FB2.2, U34.48
unnamed: J1.3, U29.10
unnamed: J2.1, U19.6
unnamed: J2.2, U20.10
unnamed: J2.3, U20.6
unnamed: J2.4, U21.10
unnamed: J2.5, U21.6
unnamed: J2.6, U22.10
unnamed: J2.8, U22.6
unnamed: J2.9, U23.10
unnamed: J2.11, U23.6
unnamed: J2.12, U24.10
unnamed: J2.13, U24.6
unnamed: J2.16, U28.6
unnamed: J2.17, U28.10
unnamed: J2.18, U27.6
unnamed: J2.20, U27.10
unnamed: J2.21, U26.6
unnamed: J2.22, U26.10
unnamed: J2.24, U25.6
unnamed: J2.26, U25.10
unnamed: J4.2, J6.1
unnamed: J4.4, J6.3
unnamed: Q1.1, R28.1, R29.1
unnamed: Q1.3, Q1.6, R30.2
unnamed: R3.1, R4.2, U2.2, U3.1
unnamed: R4.1, R5.2, U3.2, U4.1
unnamed: R5.1, R6.2, U4.2, U5.1
unnamed: R6.1, R7.2, U5.2, U6.1
unnamed: R7.1, R8.2, U6.2, U7.1
unnamed: R8.1, R9.2, U7.2, U8.1
unnamed: R9.1, R10.2, U8.2, U9.1
unnamed: R11.1, U11.1
unnamed: R11.2, R13.1, R14.1, U10.6
unnamed: R12.2, U11.6
unnamed: R22.2, U13.5
unnamed: R23.2, U10.1, U10.2
unnamed: CURRENT.2, R24.2, U13.7
unnamed: R25.1, U10.3
unnamed: R25.2, R26.1, R27.2, V+.1
unnamed: R31.2, U20.9
unnamed: R32.2, U20.7
unnamed: R33.2, U21.9
unnamed: R34.2, U21.7
unnamed: R35.2, U22.9
unnamed: R36.2, U22.7
unnamed: R37.2, U23.9
unnamed: R38.2, U23.7
unnamed: R39.2, U24.9
unnamed: R40.2, U24.7
unnamed: R41.2, U25.9
unnamed: R42.2, U25.7
unnamed: R43.2, U26.9
unnamed: R44.2, U26.7
unnamed: R45.2, U27.9
unnamed: R46.2, U27.7
unnamed: R47.2, U28.9
unnamed: R48.2, U28.7
unnamed: R49.2, U29.9
unnamed: R50.2, U29.7
unnamed: R51.1, R52.1, U29.6
unnamed: R51.2, U30.4
unnamed: R52.2, U30.1, U30.2, U30.9
unnamed: CLK.2, U12.17, X1.3
unnamed: U1.1, U3.4
unnamed: U1.2, U4.4
unnamed: U1.3, U5.4
unnamed: U1.4, U6.4
unnamed: U1.5, U7.4
unnamed: U1.6, U8.4
unnamed: U1.7, U9.4
unnamed: U1.15, U2.4
unnamed: U14.1, U18.14, U29.1
unnamed: U14.3, U18.15, U29.5
unnamed: U14.4, U19.1, U19.5
unnamed: U15.4, U16.2
unnamed: U16.3, U17.10
unnamed: U16.4, U17.13
unnamed: U16.5, U17.12
unnamed: U16.6, U17.11
unnamed: U16.11, U18.10
unnamed: U16.12, U18.13
unnamed: U16.13, U18.12
unnamed: U16.14, U18.11
unnamed: U17.1, U23.5
unnamed: U17.2, U23.1
unnamed: U17.3, U22.5
unnamed: U17.4, U22.1
unnamed: U17.5, U21.5
unnamed: U17.6, U21.1
unnamed: U17.7, U20.5
unnamed: U17.9, U20.1
unnamed: U17.14, U24.1
unnamed: U17.15, U24.5
unnamed: U18.1, U28.5
unnamed: U18.2, U28.1
unnamed: U18.3, U27.5
unnamed: U18.4, U27.1
unnamed: U18.5, U26.5
unnamed: U18.6, U26.1
unnamed: U18.7, U25.5
unnamed: U18.9, U25.1
unnamed: U19.10, U20.2, U20.4, U21.2, U21.4, U22.2, U22.4, U23.2, U23.4, U24.2, U24.4, U25.2, U25.4, U26.2, U26.4, U27.2, U27.4, U28.2, U28.4, U29.2, U29.4
PAYLOAD_RST: C50.2, J3.5, J4.11, R57.1, U34.23
RX_IN: J3.4, U34.21
TCK: J4.7, U34.15
TDI: J4.3, U34.13
TDO: J4.1, U34.12
TEST: J4.8, U34.22
TMS: J4.5, U34.14
TX_OUT: J3.3, U34.20

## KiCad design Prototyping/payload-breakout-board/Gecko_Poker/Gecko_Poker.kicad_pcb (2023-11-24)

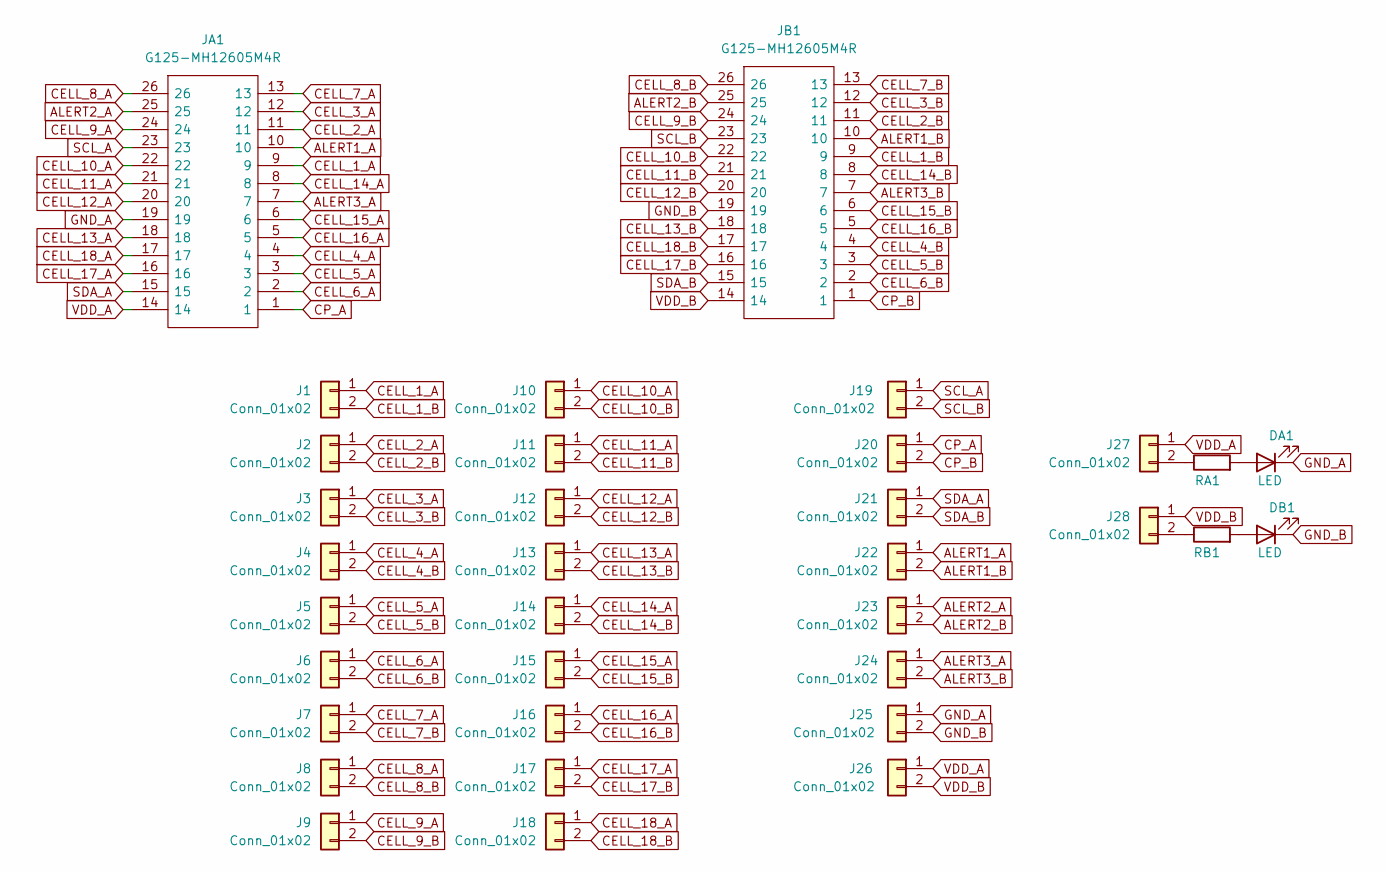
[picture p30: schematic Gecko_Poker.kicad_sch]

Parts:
DA1: LED; LED_0805_2012Metric
DB1: LED; LED_0805_2012Metric
J1, J2, J3, J4, J5, J6, J7, J8, J9, J10, J11, J12, J13, J14, J15, J16, J17, J18, J19, J20, J21, J22, J23, J24, J25, J26, J27, J28: Conn_01x02; PinHeader_1x02_P2.54mm_Vertical
JA1: G125-MH12605M4R; G125-MV12605M1P; Manufacturer_Part_Number G125-MH12605M4R; Mouser Part Number 855-G125MH1265M4RM4R
JB1: G125-MH12605M4R; G125-MV12605M1P; Manufacturer_Part_Number G125-MH12605M4R; Mouser Part Number 855-G125MH1265M4RM4R
RA1: (no value)
RB1: (no value)

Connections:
ALERT1_A: J22.1, JA1.10
ALERT1_B: J22.2, JB1.10
ALERT2_A: J23.1, JA1.25
ALERT2_B: J23.2, JB1.25
ALERT3_A: J24.1, JA1.7
ALERT3_B: J24.2, JB1.7
CELL_1_A: J1.1, JA1.9
CELL_1_B: J1.2, JB1.9
CELL_2_A: J2.1, JA1.11
CELL_2_B: J2.2, JB1.11
CELL_3_A: J3.1, JA1.12
CELL_3_B: J3.2, JB1.12
CELL_4_A: J4.1, JA1.4
CELL_4_B: J4.2, JB1.4
CELL_5_A: J5.1, JA1.3
CELL_5_B: J5.2, JB1.3
CELL_6_A: J6.1, JA1.2
CELL_6_B: J6.2, JB1.2
CELL_7_A: J7.1, JA1.13
CELL_7_B: J7.2, JB1.13
CELL_8_A: J8.1, JA1.26
CELL_8_B: J8.2, JB1.26
CELL_9_A: J9.1, JA1.24
CELL_9_B: J9.2, JB1.24
CELL_10_A: J10.1, JA1.22
CELL_10_B: J10.2, JB1.22
CELL_11_A: J11.1, JA1.21
CELL_11_B: J11.2, JB1.21
CELL_12_A: J12.1, JA1.20
CELL_12_B: J12.2, JB1.20
CELL_13_A: J13.1, JA1.18
CELL_13_B: J13.2, JB1.18
CELL_14_A: J14.1, JA1.8
CELL_14_B: J14.2, JB1.8
CELL_15_A: J15.1, JA1.6
CELL_15_B: J15.2, JB1.6
CELL_16_A: J16.1, JA1.5
CELL_16_B: J16.2, JB1.5
CELL_17_A: J17.1, JA1.16
CELL_17_B: J17.2, JB1.16
CELL_18_A: J18.1, JA1.17
CELL_18_B: J18.2, JB1.17
CP_A: J20.1, JA1.1
CP_B: J20.2, JB1.1
GND_A: DA1.1 (K), J25.1, JA1.19
GND_B: DB1.1 (K), J25.2, JB1.19
unnamed: DA1.2 (A), RA1.2
unnamed: DB1.2 (A), RB1.2
unnamed: J27.2, RA1.1
unnamed: J28.2, RB1.1
SCL_A: J19.1, JA1.23
SCL_B: J19.2, JB1.23
SDA_A: J21.1, JA1.15
SDA_B: J21.2, JB1.15
VDD_A: J26.1, J27.1, JA1.14
VDD_B: J26.2, J28.1, JB1.14

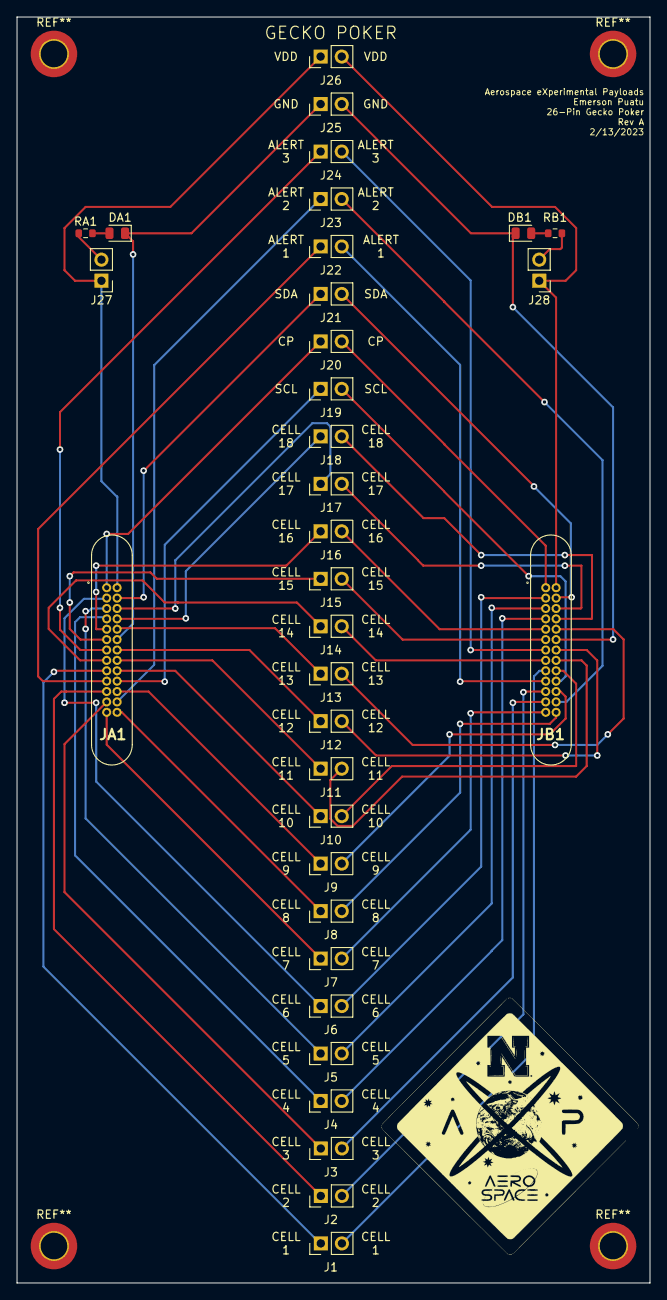
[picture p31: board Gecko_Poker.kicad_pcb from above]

Board: 2 copper layers, 76.2 x 152.4 mm, 34 parts (0 on the bottom side), 56 nets.

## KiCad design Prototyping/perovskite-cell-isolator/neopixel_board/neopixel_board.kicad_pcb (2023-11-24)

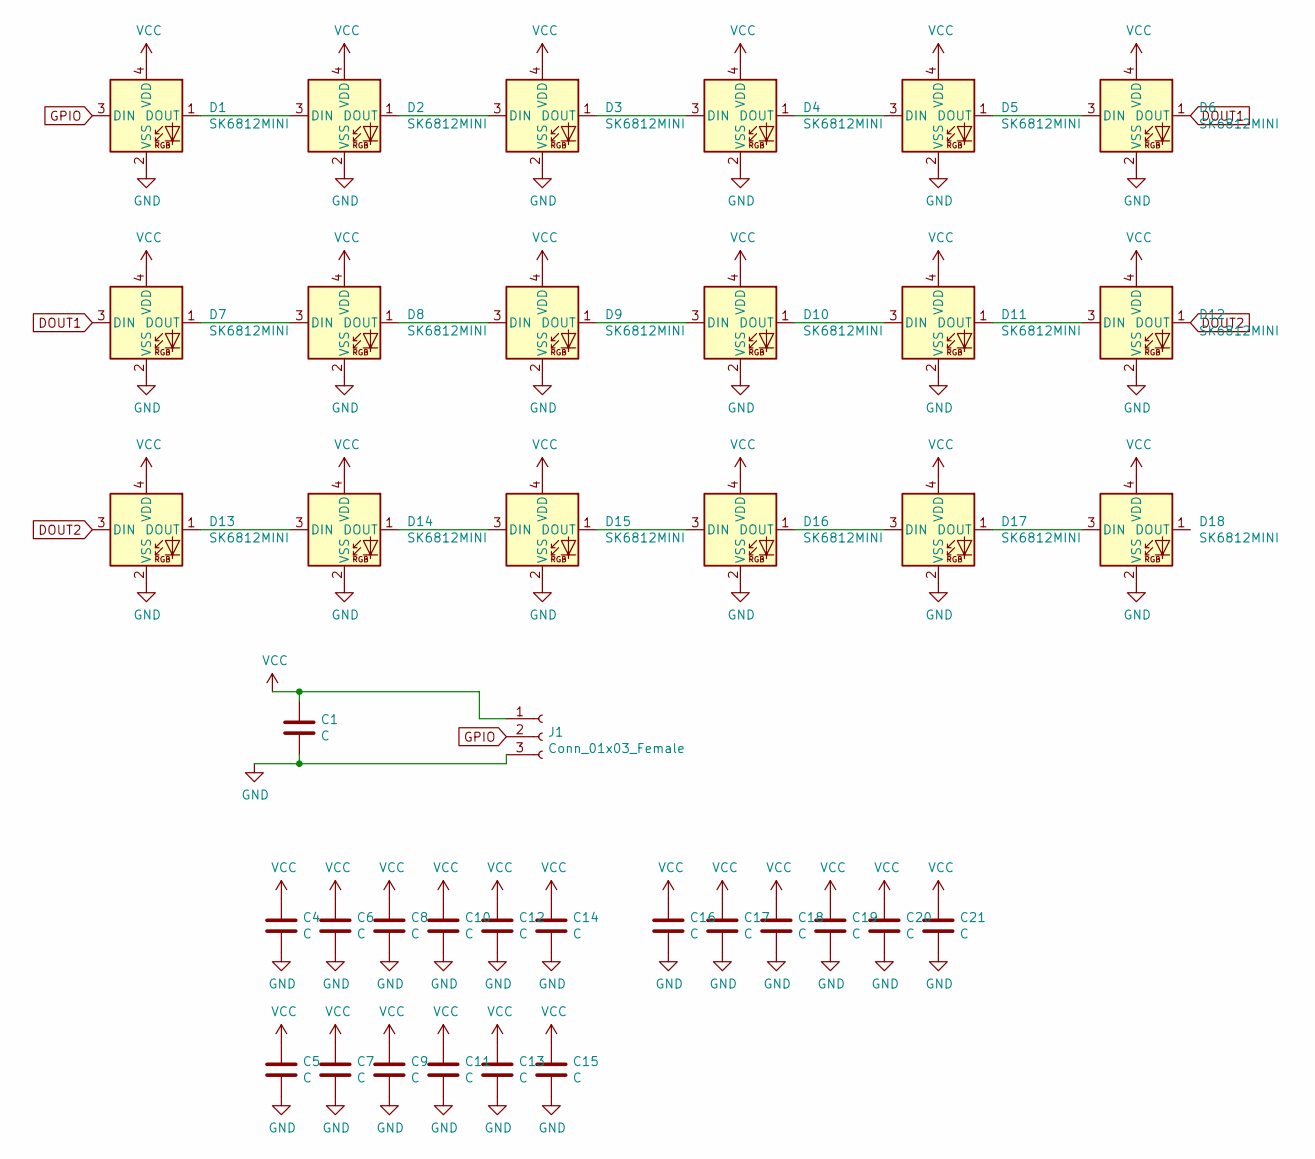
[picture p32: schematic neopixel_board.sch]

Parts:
C1: C; CP_Radial_D10.0mm_P5.00mm
C4, C5, C6, C7, C8, C9, C10, C11, C12, C13, C14, C15, C16, C17, C18, C19, C20, C21: C; C_0805_2012Metric
D1, D2, D3, D4, D5, D6, D7, D8, D9, D10, D11, D12, D13, D14, D15, D16, D17, D18: SK6812MINI; LED_SK6812MINI_PLCC4_3.5x3.5mm_P1.75mm
J1: Conn_01x03_Female; PinHeader_1x03_P2.54mm_Vertical

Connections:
DOUT1: D6.1 (DOUT), D7.3 (DIN)
DOUT2: D12.1 (DOUT), D13.3 (DIN)
GND: C1.2, C4.2, C5.2, C6.2, C7.2, C8.2, C9.2, C10.2, C11.2, C12.2, C13.2, C14.2, C15.2, C16.2, C17.2, C18.2, C19.2, C20.2, C21.2, D1.2 (VSS), D2.2 (VSS), D3.2 (VSS), D4.2 (VSS), D5.2 (VSS), D6.2 (VSS), D7.2 (VSS), D8.2 (VSS), D9.2 (VSS), D10.2 (VSS), D11.2 (VSS), D12.2 (VSS), D13.2 (VSS), D14.2 (VSS), D15.2 (VSS), D16.2 (VSS), D17.2 (VSS), D18.2 (VSS), J1.3; also elsewhere on the board
GPIO: D1.3 (DIN), J1.2
unnamed: D1.1 (DOUT), D2.3 (DIN)
unnamed: D2.1 (DOUT), D3.3 (DIN)
unnamed: D3.1 (DOUT), D4.3 (DIN)
unnamed: D4.1 (DOUT), D5.3 (DIN)
unnamed: D5.1 (DOUT), D6.3 (DIN)
unnamed: D7.1 (DOUT), D8.3 (DIN)
unnamed: D8.1 (DOUT), D9.3 (DIN)
unnamed: D10.1 (DOUT), D11.3 (DIN)
unnamed: D9.1 (DOUT), D10.3 (DIN)
unnamed: D11.1 (DOUT), D12.3 (DIN)
unnamed: D13.1 (DOUT), D14.3 (DIN)
unnamed: D14.1 (DOUT), D15.3 (DIN)
unnamed: D15.1 (DOUT), D16.3 (DIN)
unnamed: D16.1 (DOUT), D17.3 (DIN)
unnamed: D17.1 (DOUT), D18.3 (DIN)
VCC: C1.1, C4.1, C5.1, C6.1, C7.1, C8.1, C9.1, C10.1, C11.1, C12.1, C13.1, C14.1, C15.1, C16.1, C17.1, C18.1, C19.1, C20.1, C21.1, D1.4 (VDD), D2.4 (VDD), D3.4 (VDD), D4.4 (VDD), D5.4 (VDD), D6.4 (VDD), D7.4 (VDD), D8.4 (VDD), D9.4 (VDD), D10.4 (VDD), D11.4 (VDD), D12.4 (VDD), D13.4 (VDD), D14.4 (VDD), D15.4 (VDD), D16.4 (VDD), D17.4 (VDD), D18.4 (VDD), J1.1; also elsewhere on the board

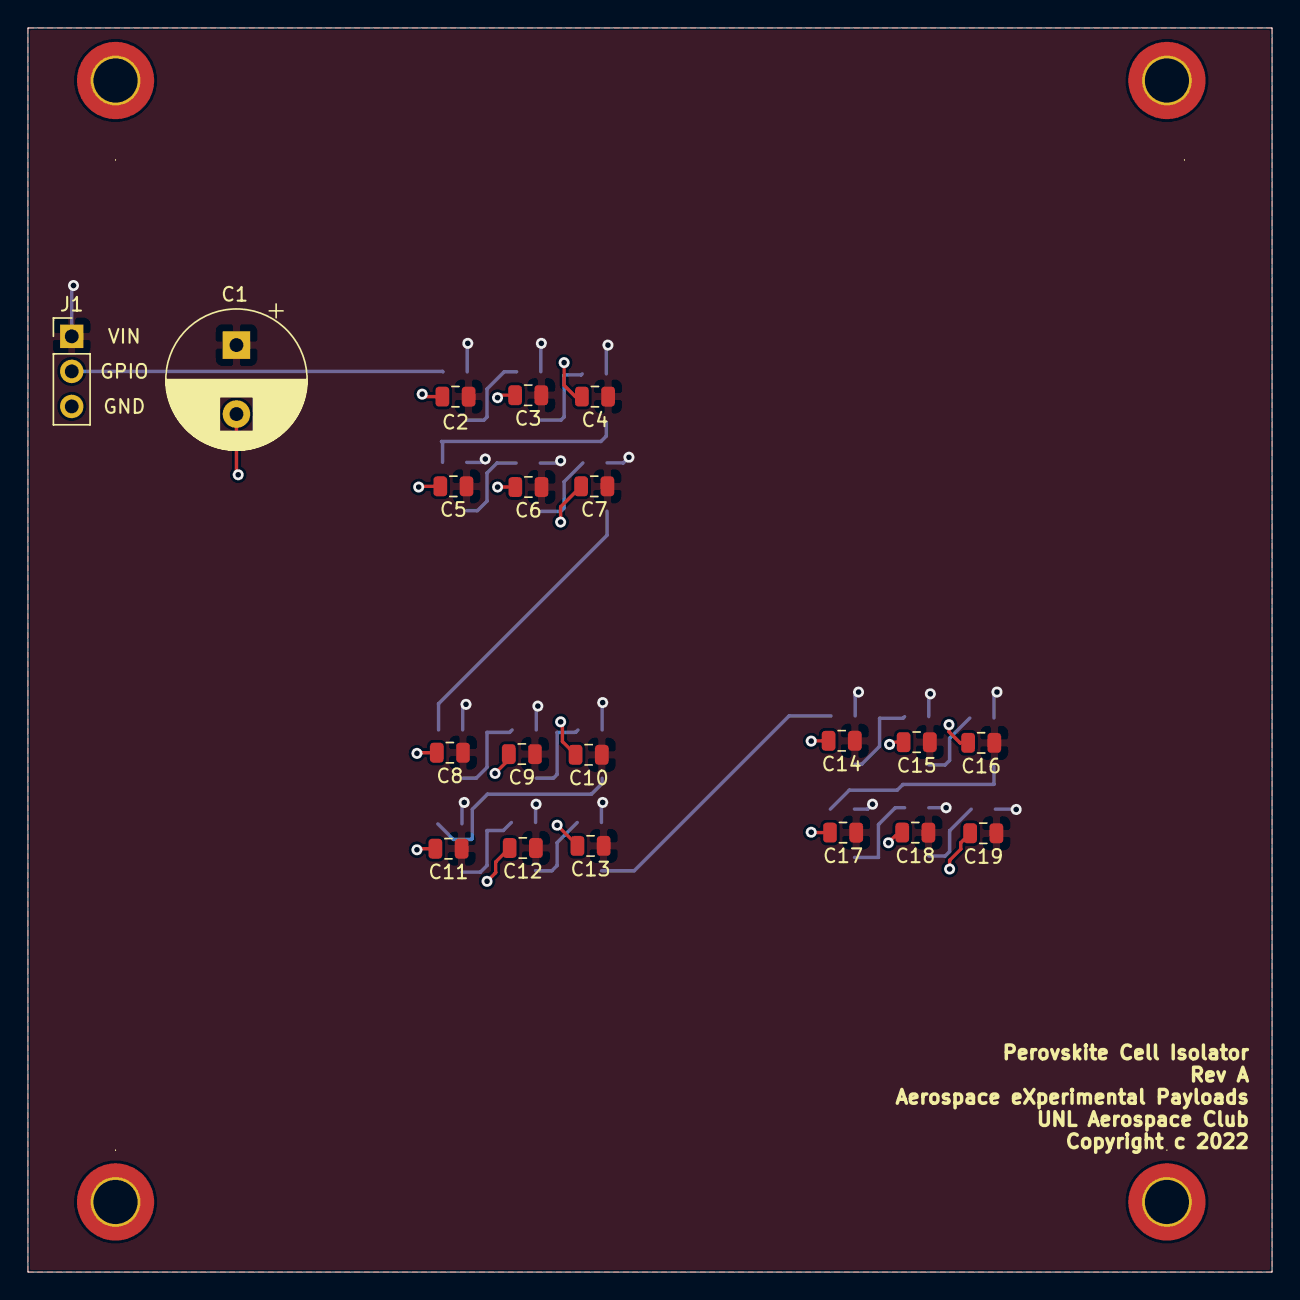
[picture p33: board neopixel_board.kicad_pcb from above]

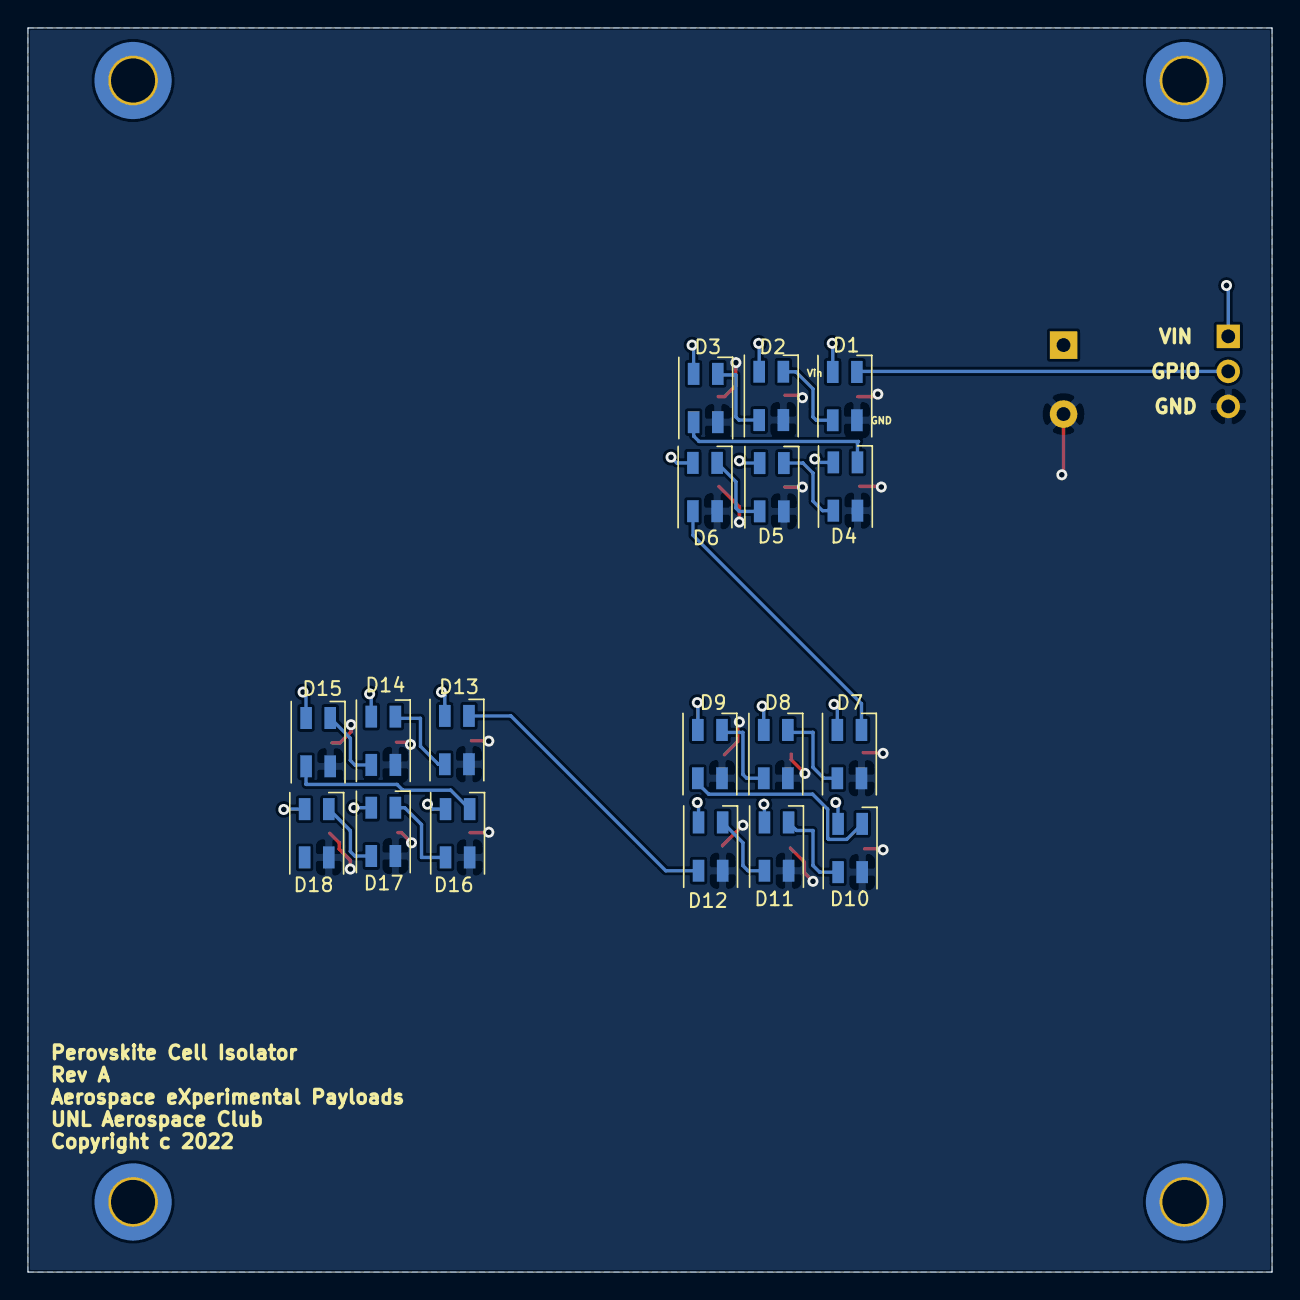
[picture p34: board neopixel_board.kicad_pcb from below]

Board: 2 copper layers, 90.2 x 90.2 mm, 42 parts (18 on the bottom side), 20 nets.

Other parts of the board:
., .#2, .#3, .#4: MountingHole_3.2mm_M3_DIN965_Pad_TopBottom
C2, C3: C; C_0805_2012Metric

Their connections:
GND: C2.2, C3.2; also elsewhere on the board
VCC: C2.1, C3.1; also elsewhere on the board

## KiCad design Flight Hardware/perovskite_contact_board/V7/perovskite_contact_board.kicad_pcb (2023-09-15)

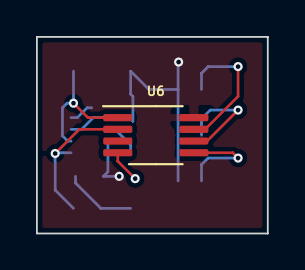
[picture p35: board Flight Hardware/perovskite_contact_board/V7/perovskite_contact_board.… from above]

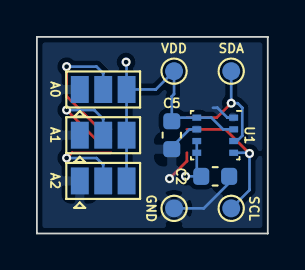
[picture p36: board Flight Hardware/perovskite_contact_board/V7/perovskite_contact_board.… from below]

Board: 2 copper layers, 12.8 x 10.9 mm, 11 parts (10 on the bottom side), 7 nets.

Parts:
A0, A1, A2: Jumper_3_Open; SolderJumper-3_P1.3mm_Open_Pad1.0x1.5mm
C2, C5: 0.1u; C_0603_1608Metric
JP103.1, JP103.10, JP103.11, JP103.12: Conn_01x01; TestPoint_Pad_D1.0mm
U1: BME280; Bosch_LGA-8_2.5x2.5mm_P0.65mm_ClockwisePinNumbering
U6: MCP9808_MSOP; MSOP-8_3x3mm_P0.65mm

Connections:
GND: A0.1, A1.1, A2.1, C2.2, C5.2, JP103.1.1, U1.1, U1.7, U6.4
unnamed: A2.2, U6.5
unnamed: A1.2, U6.6
unnamed: A0.2, U6.7
SCL: JP103.11.1, U1.4, U6.2
SDA: JP103.12.1, U1.3, U6.1
VDDF: A0.3, A1.3, A2.3, C2.1, C5.1, JP103.10.1, U1.2, U1.5, U1.6, U1.8, U6.8

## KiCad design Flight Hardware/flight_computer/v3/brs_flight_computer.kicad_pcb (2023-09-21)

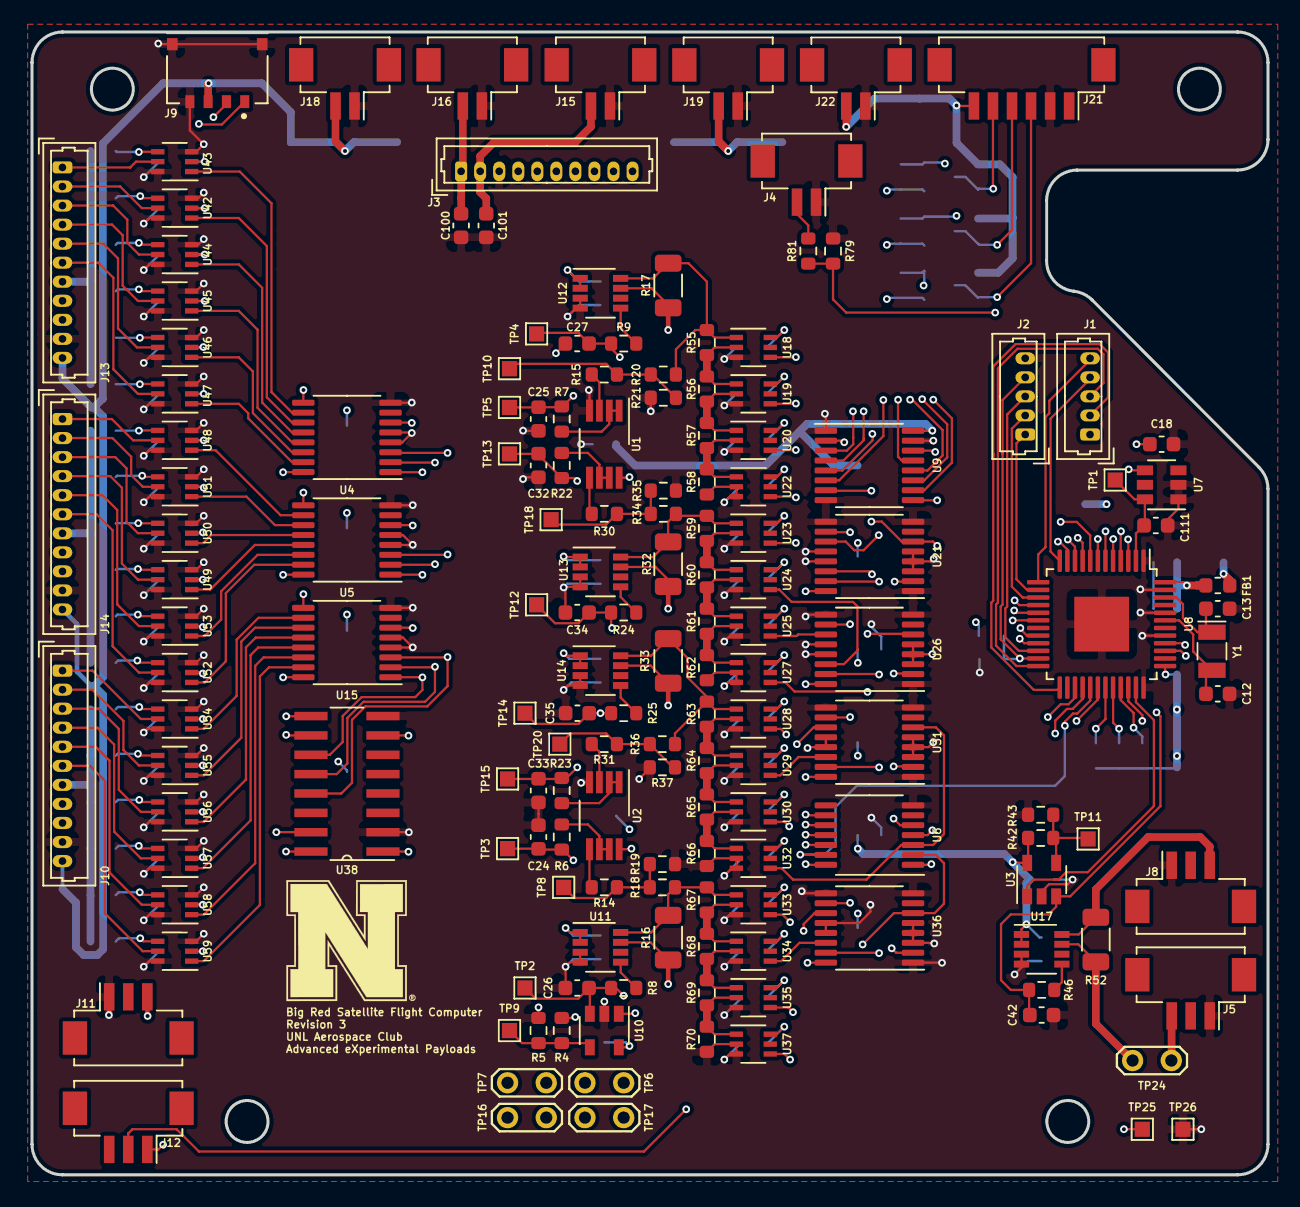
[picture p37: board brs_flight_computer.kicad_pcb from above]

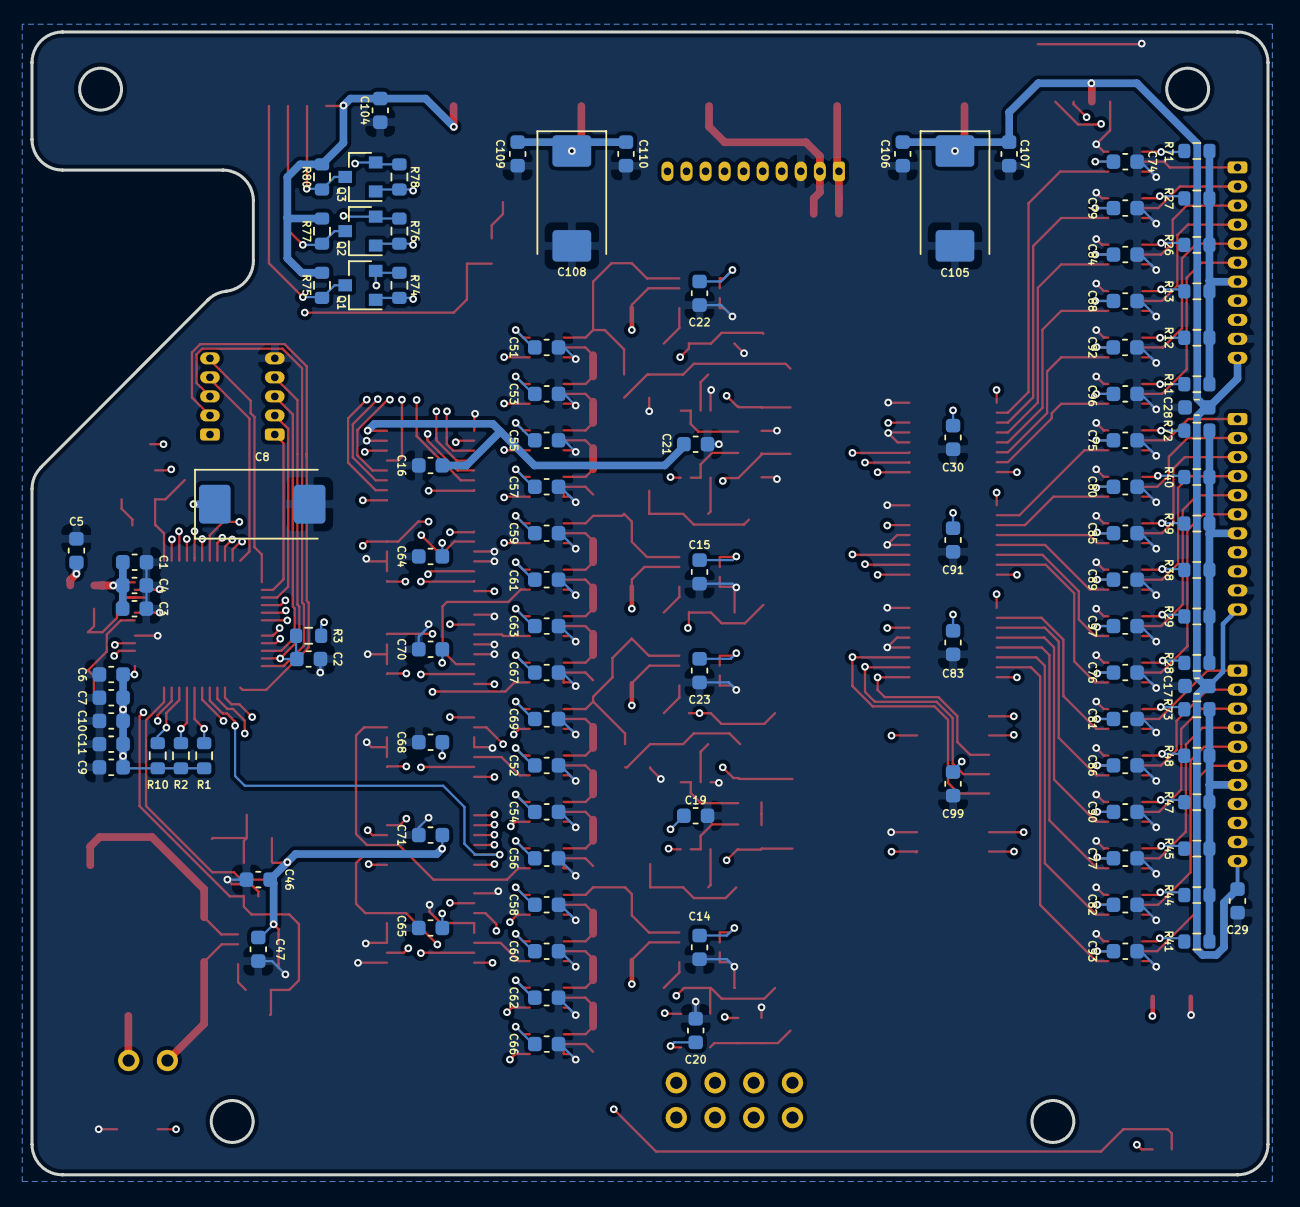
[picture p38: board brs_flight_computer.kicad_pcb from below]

Board: 4 copper layers, 81.1 x 75.0 mm, 265 parts (105 on the bottom side), 177 nets.

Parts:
C1, C10, C100, C106, C109: 10u; C_0603_1608Metric
C2, C4, C5, C6, C9, C11, C14, C15, C16, C17, C18, C19, C20, C21, C22, C23, C28, C29, C30, C51, C52, C53, C54, C55, C56, C57, C58, C59, C60, C61, C62, C63, C64, C65, C66, C67, C68, C69, C70, C71, C74, C75, C76, C77, C79, C80, C81, C82, C83, C84, C85, C86, C88, C89, C90, C91, C92, C93, C96, C97, C99, C101, C104, C107, C110, C111: 0.1u; C_0603_1608Metric
C3, C7, C46, C47: 1u; C_0603_1608Metric
C8, C105, C108: 47u; CP_EIA-7343-43_Kemet-X
C12, C13: 10p; C_0603_1608Metric
C24, C25, C26, C27, C32, C33, C34, C35, C42: 10n; C_0603_1608Metric
FB1: Ferrite_Bead_Small; L_0603_1608Metric
J1, J2: Conn_01x05_Male; Molex_PicoBlade_53047-0510_1x05_P1.25mm_Vertical
J3: Conn_01x10_Male; Molex_PicoBlade_53047-1010_1x10_P1.25mm_Vertical
J4: BUSS; Hirose_DF13C_CL535-0402-2-51_1x02-1MP_P1.25mm_Vertical
J5: Panel 3; Hirose_DF13C_CL535-0403-5-51_1x03-1MP_P1.25mm_Vertical
J8: Conn_01x03_Male; Hirose_DF13C_CL535-0403-5-51_1x03-1MP_P1.25mm_Vertical
J9: 0781710004; MOLEX_0781710004
J10: Perovskite 3; Molex_PicoBlade_53047-1110_1x11_P1.25mm_Vertical
J11: GaAs Panel; Hirose_DF13C_CL535-0403-5-51_1x03-1MP_P1.25mm_Vertical
J12: GaAs Temperature; Hirose_DF13C_CL535-0403-5-51_1x03-1MP_P1.25mm_Vertical
J13: Perovskite 1; Molex_PicoBlade_53047-1110_1x11_P1.25mm_Vertical
J14: Perovskite 2; Molex_PicoBlade_53047-1110_1x11_P1.25mm_Vertical
J15, J16, J18, J19, J22: Power; Hirose_DF13C_CL535-0402-2-51_1x02-1MP_P1.25mm_Vertical
J21: EPS Serial; Hirose_DF13C_CL535-0406-3-51_1x06-1MP_P1.25mm_Vertical
Q1, Q2, Q3: BSS138; SOT-23
R1, R2, R10: 4k7; R_0603_1608Metric
R3, R74, R75, R76, R77, R78, R80: 10k; R_0603_1608Metric
R4, R5, R6, R7, R8, R9, R14, R15, R22, R23, R24, R25, R30, R31, R42, R43, R46: 470; R_0603_1608Metric
R11, R12, R13, R26, R27, R28, R29, R38, R39, R40, R41, R44, R45, R47, R48, R71, R72, R73: 400; R_0603_1608Metric
R16, R17, R32, R33, R52: 510m; R_1206_3216Metric
R18, R81: 3M; R_0603_1608Metric
R19, R20, R21, R34, R35, R36, R37, R55, R59, R63, R67, R79: 1M; R_0603_1608Metric
R56, R60, R64, R68: 430; R_0603_1608Metric
R57, R61, R65, R69: 270; R_0603_1608Metric
R58, R62, R66, R70: 120; R_0603_1608Metric
TP1: VREF; TestPoint_Pad_1.0x1.0mm
TP2, TP4, TP11, TP12, TP14: I; TestPoint_Pad_1.0x1.0mm
TP3, TP5, TP13, TP15: V; TestPoint_Pad_1.0x1.0mm
TP6, TP7, TP16, TP17, TP24: Current Test; TestPoint_2Pads_Pitch2.54mm_Drill0.8mm
TP8, TP9, TP10, TP18, TP20: Voltage Test+; TestPoint_Pad_1.0x1.0mm
TP25: 3V3; TestPoint_Pad_1.0x1.0mm
TP26: GND; TestPoint_Pad_1.0x1.0mm
U1, U2: OPA2387; VSSOP-8_3.0x3.0mm_P0.65mm
U3, U10: TLV7031DBV; SOT-23-5
U4, U5, U15: 74HC237; TSSOP-16_4.4x5mm_P0.65mm
U6: 4012; TSSOP-14_4.4x5mm_P0.65mm
U7: LT6654AHS6-3.3; SOT-23-6
U8: MSP430FR5969IRGZR; LQFP-48-1EP_7x7mm_P0.5mm_EP3.6x3.6mm
U9: SN74CBT3253; TSSOP-16_4.4x5mm_P0.65mm
U11, U12, U13, U14, U17: INA190A4IDDFR
U18, U19, U20, U22, U23, U24, U25, U27, U28, U29, U30, U32, U33, U34, U35, U37: ADG841YKSZ-500RL7
U21, U26, U31, U36: CD4516B_PW_16; TSSOP-16_4.4x5mm_P0.65mm
U38: CD4518BM96
U42, U43, U44, U45, U46, U47, U48, U49, U50, U51, U52, U53, U54, U55, U56, U57, U58, U59: ADG839YKSZ-REEL7
Y1: CM8V-T1A; Crystal_SMD_MicroCrystal_CC7V-T1A-2Pin_3.2x1.5mm

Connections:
+3V3: C5.1, C6.1, C7.1, C8.1, C9.2, C10.2, C11.2, C14.1, C16.1, C18.2, C20.1, C21.1, C30.1, C58.1, C60.1, C62.1, C65.1, C66.1, C74.1, C75.1, C76.1, C77.1, C79.1, C80.1, C81.1, C82.1, C83.1, C84.1, C85.1, C86.1, C88.1, C89.1, C90.1, C91.1, C92.1, C93.1, C96.1, C97.1, C99.1, C108.1, C109.1, C110.1, FB1.1, J1.1, J12.1, J19.2, Q1.1, Q2.1, Q3.1, R1.2, R2.2, R3.2, R4.1, R10.2, R74.2, R76.2, R78.2, TP25.1, U2.8, U4.6, U4.16, U5.6, U5.16, U6.12, U7.4, U8.37, U9.16, U10.5, U11.1, U11.2, U15.6, U15.16, U33.6, U34.6, U35.6, U36.16, U37.6, U38.1, U38.7, U38.10, U38.16, U42.2, U43.2, U44.2, U45.2, U46.2, U47.2, U48.2, U49.2, U50.2, U51.2, U52.2, U53.2, U54.2, U55.2, U56.2, U57.2, U58.2, U59.2
+5V: C104.1, J21.6, J22.2, R75.2, R77.2, R80.2
/Curve Tracer/GAAS_LADDER: R16.1, R18.2, R67.2, U11.8, U33.1
/Curve Tracer/GAAS_ON: U8.28, U10.1
/Curve Tracer/GAAS_POS: J11.3, TP6.1
/Curve Tracer/P_1_LADDER: R17.2, R20.2, R55.2, U12.8, U18.1
/Curve Tracer/P_2_LADDER: R32.1, R34.2, R59.2, U13.8, U23.1
/Curve Tracer/P_3_LADDER: R33.2, R36.2, R63.2, U14.8, U28.1
/Curve Tracer/READ_CURRENT: U8.10, U9.7
/Curve Tracer/READ_VOLTAGE: U8.11, U9.9
/Curve Tracer/S0_CT: U8.8, U9.14
/Curve Tracer/S1_CT: U8.9, U9.2
/EPS Connections/BUSY: Q1.2, R74.1, U8.34
/EPS Connections/READ_BUSS: R79.1, R81.1, U8.16
/EPS Connections/RX: Q3.2, R78.1, U8.21
/EPS Connections/TX: Q2.2, R76.1, U8.20
/Ground Switcher/GAAS_TEMP: J12.2, R10.1, U8.33
/Ground Switcher/MUX_CLOCK: U8.30, U38.9
/Ground Switcher/MUX_GOOD: U6.13, U8.29
/Ground Switcher/MUX_RESET: U8.39, U38.15
/Ground Switcher/SCL: J3.4, J9.2, J10.9, J13.9, J14.9, R2.1, U8.32
/Ground Switcher/SDA: J3.5, J9.1, J10.8, J13.8, J14.8, R1.1, U8.31
/Microcontroller/CT_GOOD: U6.1, U8.27
/Microcontroller/LADDER_CLOCK: U8.17, U21.15, U26.15, U31.15, U36.15
/Microcontroller/MAG_INT: J3.6, U8.7
/Microcontroller/NC_V: J3.10, U8.3
/Microcontroller/NO_V: J3.9, U8.4
/Microcontroller/PANEL_3_CURRENT_V: C42.1, R46.1, U3.3, U8.40
/Microcontroller/SET: J3.7, U8.6
/Microcontroller/TRACE_DIR: U8.18, U21.10, U26.10, U31.10, U36.10
/Microcontroller/UNSET: J3.8, U8.5
/Passive ADCS/PANEL_3_CURRENT: U3.1, U8.35
GAAS_CURRENT: C26.1, R8.1, TP2.1, U9.6, U10.3
GAAS_VOLTAGE: C24.1, R6.1, TP3.1, U9.10
GND: C1.2, C2.1, C3.2, C4.2, C5.2, C6.2, C7.2, C8.2, C9.1, C10.1, C11.1, C12.2, C13.1, C14.2, C15.2, C16.2, C17.2, C18.1, C19.2, C20.2, C21.2, C22.2, C23.2, C24.2, C25.2, C26.2, C27.2, C28.2, C29.2, C30.2, C32.2, C33.2, C34.2, C35.2, C42.2, C46.2, C47.2, C51.2, C52.2, C53.2, C54.2, C55.2, C56.2, C57.2, C58.2, C59.2, C60.2, C61.2, C62.2, C63.2, C64.2, C65.2, C66.2, C67.2, C68.2, C69.2, C70.2, C71.2, C74.2, C75.2, C76.2, C77.2, C79.2, C80.2, C81.2, C82.2, C83.2, C84.2, C85.2, C86.2, C88.2, C89.2, C90.2, C91.2, C92.2, C93.2, C96.2, C97.2, C99.2, C100.2, C101.2, C104.2, C105.2, C106.2, C107.2, C108.2, C109.2, C110.2, C111.1, J2.5, J3.3, J4.1, J5.1, J8.1, J9.4, J9.S1, J9.S2, J10.10, J11.1, J13.10, J14.10, J15.1, J16.1, J18.1, J19.1, J21.2, J22.1, R5.2, R19.1, R21.1, R35.1, R37.1, R43.2, R58.1, R62.1, R66.1, R70.1, R79.2, TP26.1, U1.4, U2.4, U3.2, U4.4, U4.5, U4.8, U5.4, U5.5, U5.8, U6.7, U7.1, U7.2, U8.1, U8.36, U8.41, U8.44, U8.47, U8.49, U9.1, U9.8, U9.15, U10.2, U11.3, U11.4, U12.3, U12.4, U13.3, U13.4, U14.3, U14.4, U15.4, U15.5, U15.8, U17.3, U17.4, U18.3, U19.3, U20.3, U21.1, U21.3, U21.4, U21.5, U21.8, U21.9, U21.12, U21.13, U22.2, U22.3, U23.3, U24.3, U25.3, U26.1, U26.3, U26.4, U26.5, U26.8, U26.9, U26.12, U26.13, U27.2, U27.3, U28.3, U29.3, U30.3, U31.1, U31.3, U31.4, U31.5, U31.8, U31.9, U31.12, U31.13, U32.2, U32.3, U33.3, U34.3, U35.3, U36.1, U36.3, U36.4, U36.5, U36.8, U36.9, U36.12, U36.13, U37.2, U37.3, U38.2, U38.8, U42.3, U42.6, U43.3, U43.6, U44.3, U44.6, U45.3, U45.6, U46.3, U46.6, U47.3, U47.6, U48.3, U48.6, U49.3, U49.6, U50.3, U50.6, U51.3, U51.6, U52.3, U52.6, U53.3, U53.6, U54.3, U54.6, U55.3, U55.6, U56.3, U56.6, U57.3, U57.6, U58.3, U58.6, U59.3, U59.6
unnamed: C12.1, U8.43, Y1.2
unnamed: C13.2, U8.46, Y1.1
unnamed: C111.2, TP1.1, U7.6, U8.2
unnamed: J4.2, R81.2
unnamed: J5.3, TP24.1
unnamed: J8.3, R52.1, U17.8
unnamed: J21.3, Q1.3, R75.1
unnamed: J21.4, Q2.3, R77.1
unnamed: J21.5, Q3.3, R80.1
unnamed: R4.2, R5.1, TP9.1, U10.4
unnamed: R6.2, U2.6, U2.7
unnamed: R7.2, U1.1, U1.2
unnamed: R8.2, U11.5
unnamed: R9.2, U12.5
unnamed: R11.2, U47.4
unnamed: R12.2, U46.4
unnamed: R13.2, U45.4
unnamed: R14.1, U2.5
unnamed: R14.2, R18.1, R19.2, TP8.1
unnamed: R15.1, U1.3
unnamed: R15.2, R20.1, R21.2, TP10.1
unnamed: R16.2, TP6.2, U11.7
unnamed: R17.1, TP7.2, U12.7
unnamed: R22.2, U1.6, U1.7
unnamed: R23.2, U2.1, U2.2
unnamed: R24.2, U13.5
unnamed: R25.2, U14.5
unnamed: R26.2, U44.4
unnamed: R27.2, U42.4
unnamed: R28.2, U52.4
unnamed: R29.2, U53.4
unnamed: R30.1, U1.5
unnamed: R30.2, R34.1, R35.2, TP18.1
unnamed: R31.1, U2.3
unnamed: R31.2, R36.1, R37.2, TP20.1
unnamed: R32.2, TP16.2, U13.7
unnamed: R33.1, TP17.2, U14.7
unnamed: R38.2, U49.4
unnamed: R39.2, U50.4
unnamed: R40.2, U51.4
unnamed: R41.2, U59.4
unnamed: R42.2, R43.1, TP11.1, U3.4
unnamed: R44.2, U58.4
unnamed: R45.2, U57.4
unnamed: R46.2, U17.5
unnamed: R47.2, U56.4
unnamed: R48.2, U55.4
unnamed: R52.2, TP24.2, U17.7
unnamed: R55.1, R56.2, U18.2, U19.1
unnamed: R56.1, R57.2, U19.2, U20.1
unnamed: R57.1, R58.2, U20.2, U22.1
unnamed: R59.1, R60.2, U23.2, U24.1
unnamed: R60.1, R61.2, U24.2, U25.1
unnamed: R61.1, R62.2, U25.2, U27.1
unnamed: R63.1, R64.2, U28.2, U29.1
unnamed: R64.1, R65.2, U29.2, U30.1
unnamed: R65.1, R66.2, U30.2, U32.1
unnamed: R67.1, R68.2, U33.2, U34.1
unnamed: R68.1, R69.2, U34.2, U35.1
unnamed: R69.1, R70.2, U35.2, U37.1
unnamed: R71.2, U43.4
unnamed: R72.2, U48.4
unnamed: R73.2, U54.4
unnamed: U4.9, U6.9
unnamed: U4.10, U43.1
unnamed: U4.11, U42.1
unnamed: U4.12, U44.1
unnamed: U4.13, U45.1
unnamed: U4.14, U46.1
unnamed: U4.15, U47.1
unnamed: U5.9, U6.10
unnamed: U5.11, U51.1
unnamed: U5.12, U50.1
unnamed: U5.14, U53.1
unnamed: U5.15, U52.1
unnamed: U4.1, U5.1, U15.1, U38.11
unnamed: U4.2, U5.2, U15.2, U38.12
unnamed: U4.3, U5.3, U15.3, U38.13
unnamed: U6.11, U15.9
unnamed: U15.10, U54.1
unnamed: U15.11, U55.1
unnamed: U15.12, U56.1
unnamed: U15.13, U57.1
unnamed: U15.14, U58.1
unnamed: U15.15, U59.1
unnamed: U18.4, U21.2
unnamed: U19.4, U21.14
unnamed: U20.4, U21.11
unnamed: U6.5, U21.6, U22.4
unnamed: U23.4, U26.2
unnamed: U24.4, U26.14
unnamed: U25.4, U26.11
unnamed: U6.4, U26.6, U27.4
unnamed: U28.4, U31.2
unnamed: U29.4, U31.14
unnamed: U30.4, U31.11
unnamed: U6.3, U31.6, U32.4
unnamed: U33.4, U36.2
unnamed: U34.4, U36.14
unnamed: U35.4, U36.11
unnamed: U6.2, U36.6, U37.4
unnamed: U5.10, U48.1
unnamed: U5.13, U49.1
P1_CP: J13.7, R11.1, R12.1, R13.1, R26.1, R27.1, R71.1, TP7.1
P1_P1: J13.6, U47.5
P1_P2: J13.5, U46.5
P1_P3: J13.4, U45.5
P1_P4: J13.1, U43.5
P1_P5: J13.2, U42.5
P1_P6: J13.3, U44.5
P2_CP: J14.7, R28.1, R29.1, R38.1, R39.1, R40.1, R72.1, TP16.1
P2_P1: J14.6, U52.5
P2_P2: J14.5, U53.5
P2_P3: J14.4, U49.5
P2_P4: J14.1, U48.5
P2_P5: J14.2, U51.5
P2_P6: J14.3, U50.5
P3_CP: J10.7, R41.1, R44.1, R45.1, R47.1, R48.1, R73.1, TP17.1
P3_P1: J10.6, U59.5
P3_P2: J10.5, U58.5
P3_P3: J10.4, U57.5
P3_P4: J10.1, U54.5
P3_P5: J10.2, U55.5
P3_P6: J10.3, U56.5
PAYLOAD_RST: C2.2, J2.4, R3.1, U8.23
P_1_CURRENT: C27.1, R9.1, TP4.1, U9.3
P_1_VOLTAGE: C25.1, R7.1, TP5.1, U9.13
P_2_CURRENT: C34.1, R24.1, TP12.1, U9.4
P_2_VOLTAGE: C32.1, R22.1, TP13.1, U9.12
P_3_CURRENT: C35.1, R25.1, TP14.1, U9.5
P_3_VOLTAGE: C33.1, R23.1, TP15.1, U9.11
RX_IN: J1.2, U8.25
TCK: J2.2, U8.15
TDI: J1.5, U8.13
TDO: J1.4, U8.12
TEST: J2.3, U8.22
TMS: J2.1, U8.14
TX_OUT: J1.3, U8.24
VAA: C1.1, C3.1, C4.1, FB1.2, U8.48
VBUS: C15.1, C17.1, C19.1, C22.1, C23.1, C28.1, C29.1, C46.1, C47.1, C51.1, C52.1, C53.1, C54.1, C55.1, C56.1, C57.1, C59.1, C61.1, C63.1, C64.1, C67.1, C68.1, C69.1, C70.1, C71.1, C105.1, C106.1, C107.1, J9.3, J10.11, J13.11, J14.11, J18.2, R42.1, U1.8, U3.5, U6.14, U12.1, U12.2, U13.1, U13.2, U14.1, U14.2, U17.1, U17.2, U18.6, U19.6, U20.6, U21.16, U22.6, U23.6, U24.6, U25.6, U26.16, U27.6, U28.6, U29.6, U30.6, U31.16, U32.6
VDDF: C100.1, J3.1, J16.2
VPP: C101.1, J3.2, J15.2

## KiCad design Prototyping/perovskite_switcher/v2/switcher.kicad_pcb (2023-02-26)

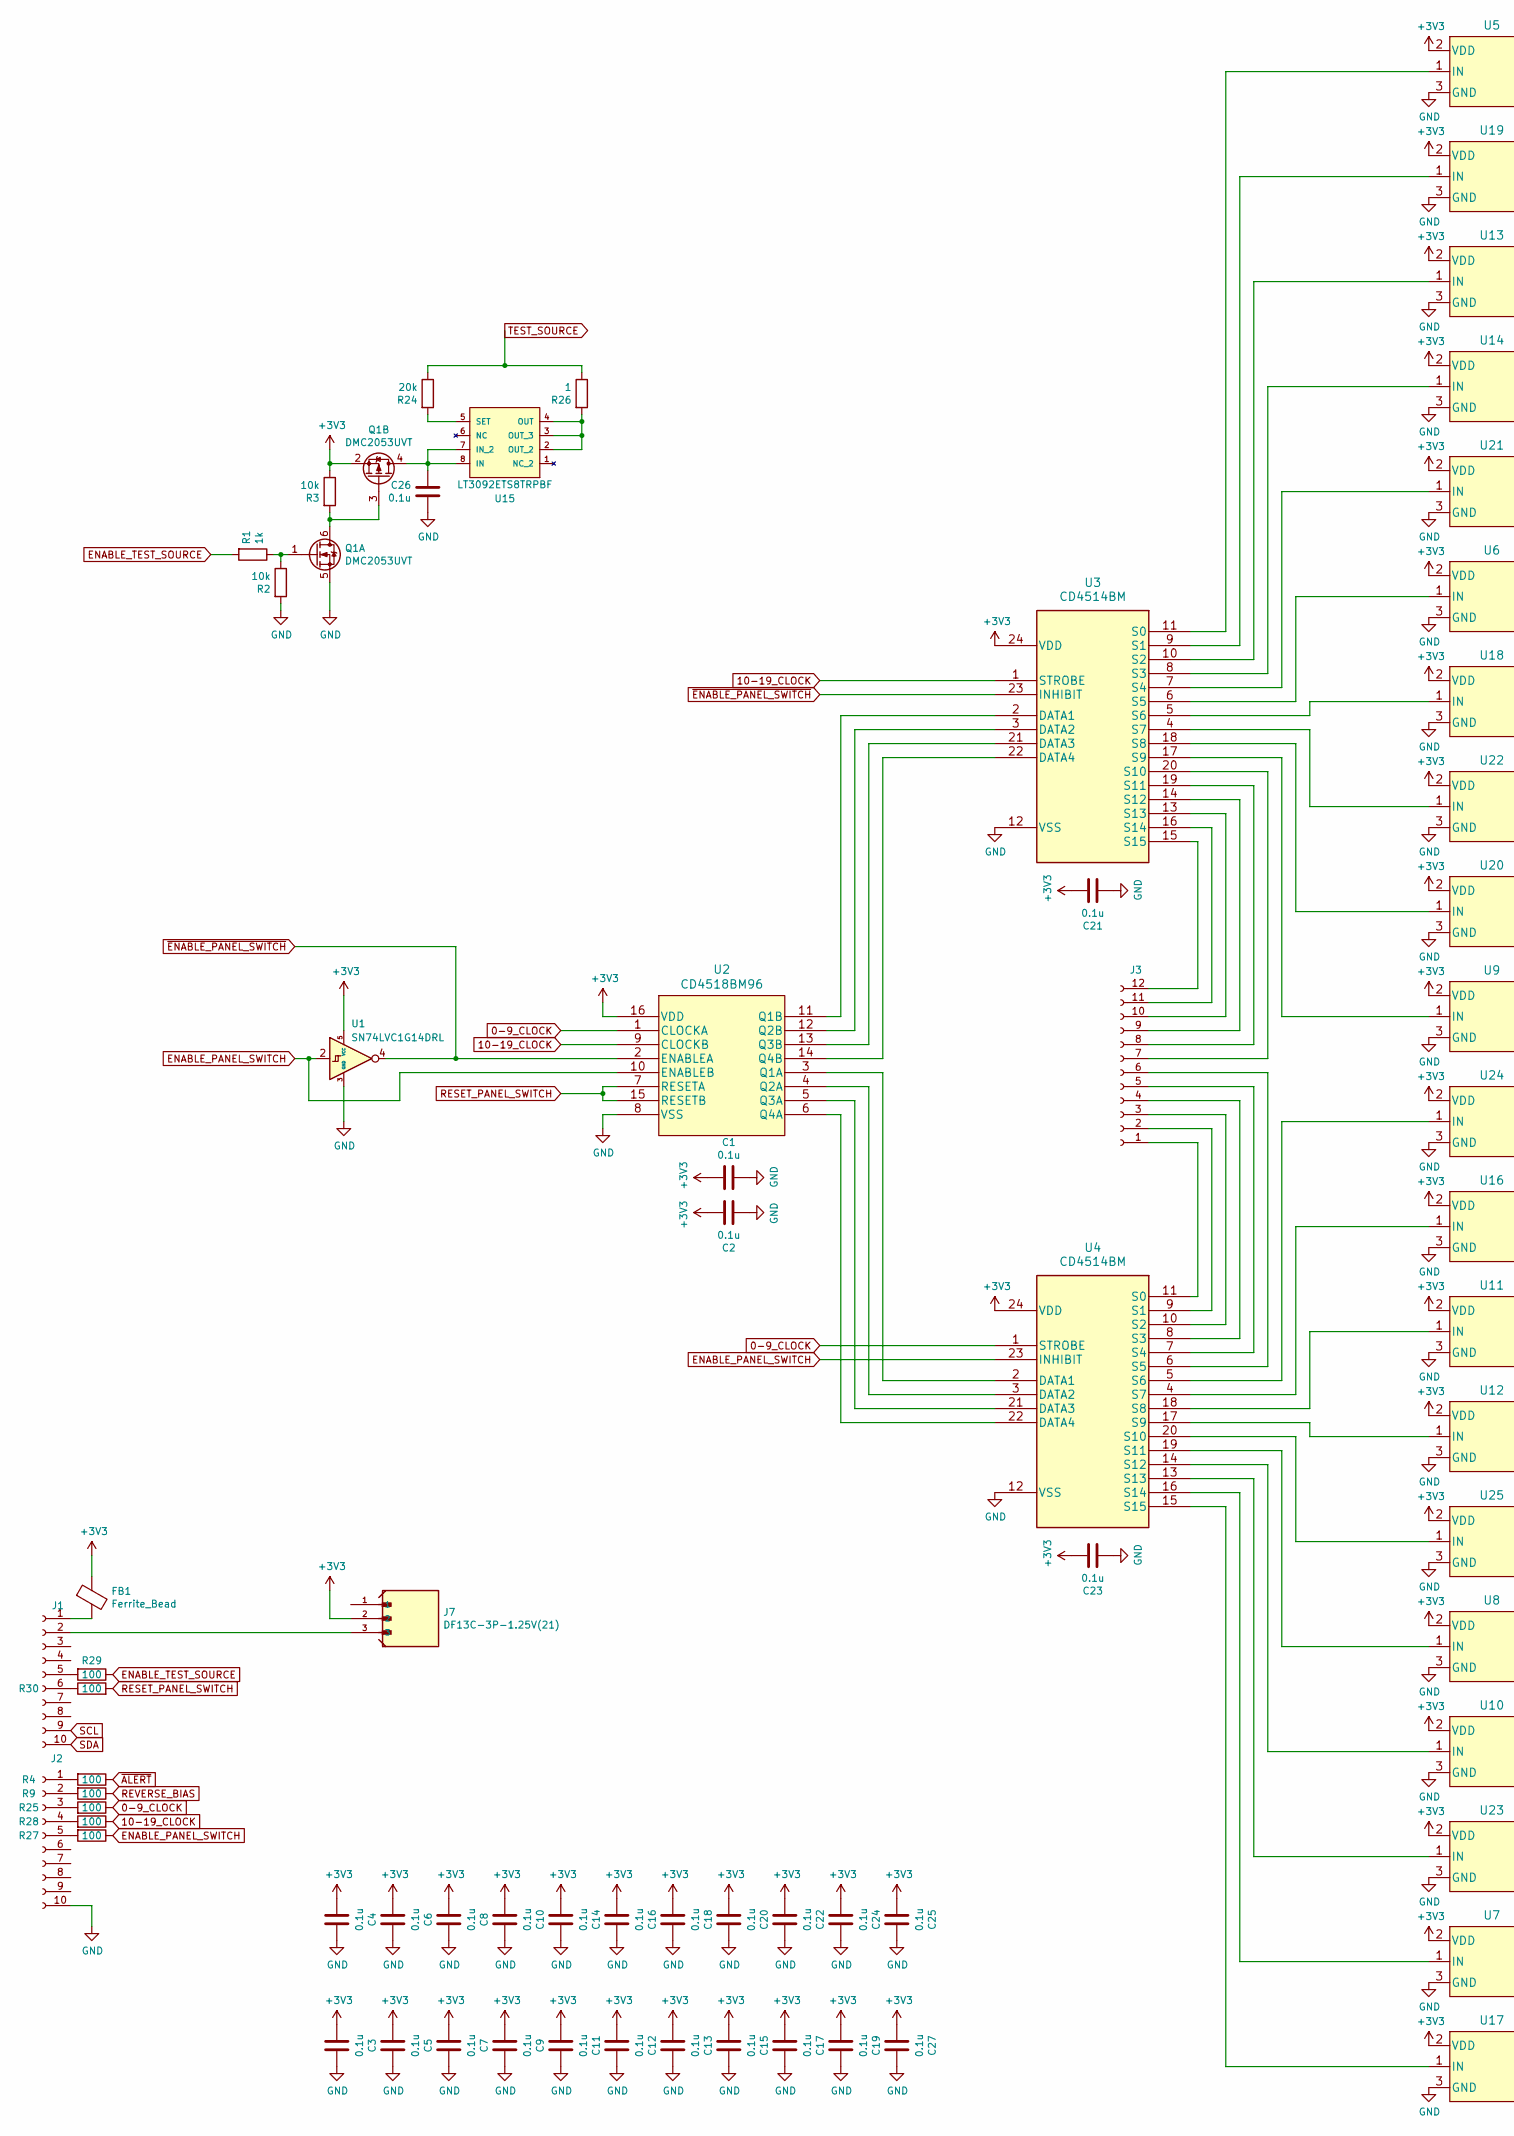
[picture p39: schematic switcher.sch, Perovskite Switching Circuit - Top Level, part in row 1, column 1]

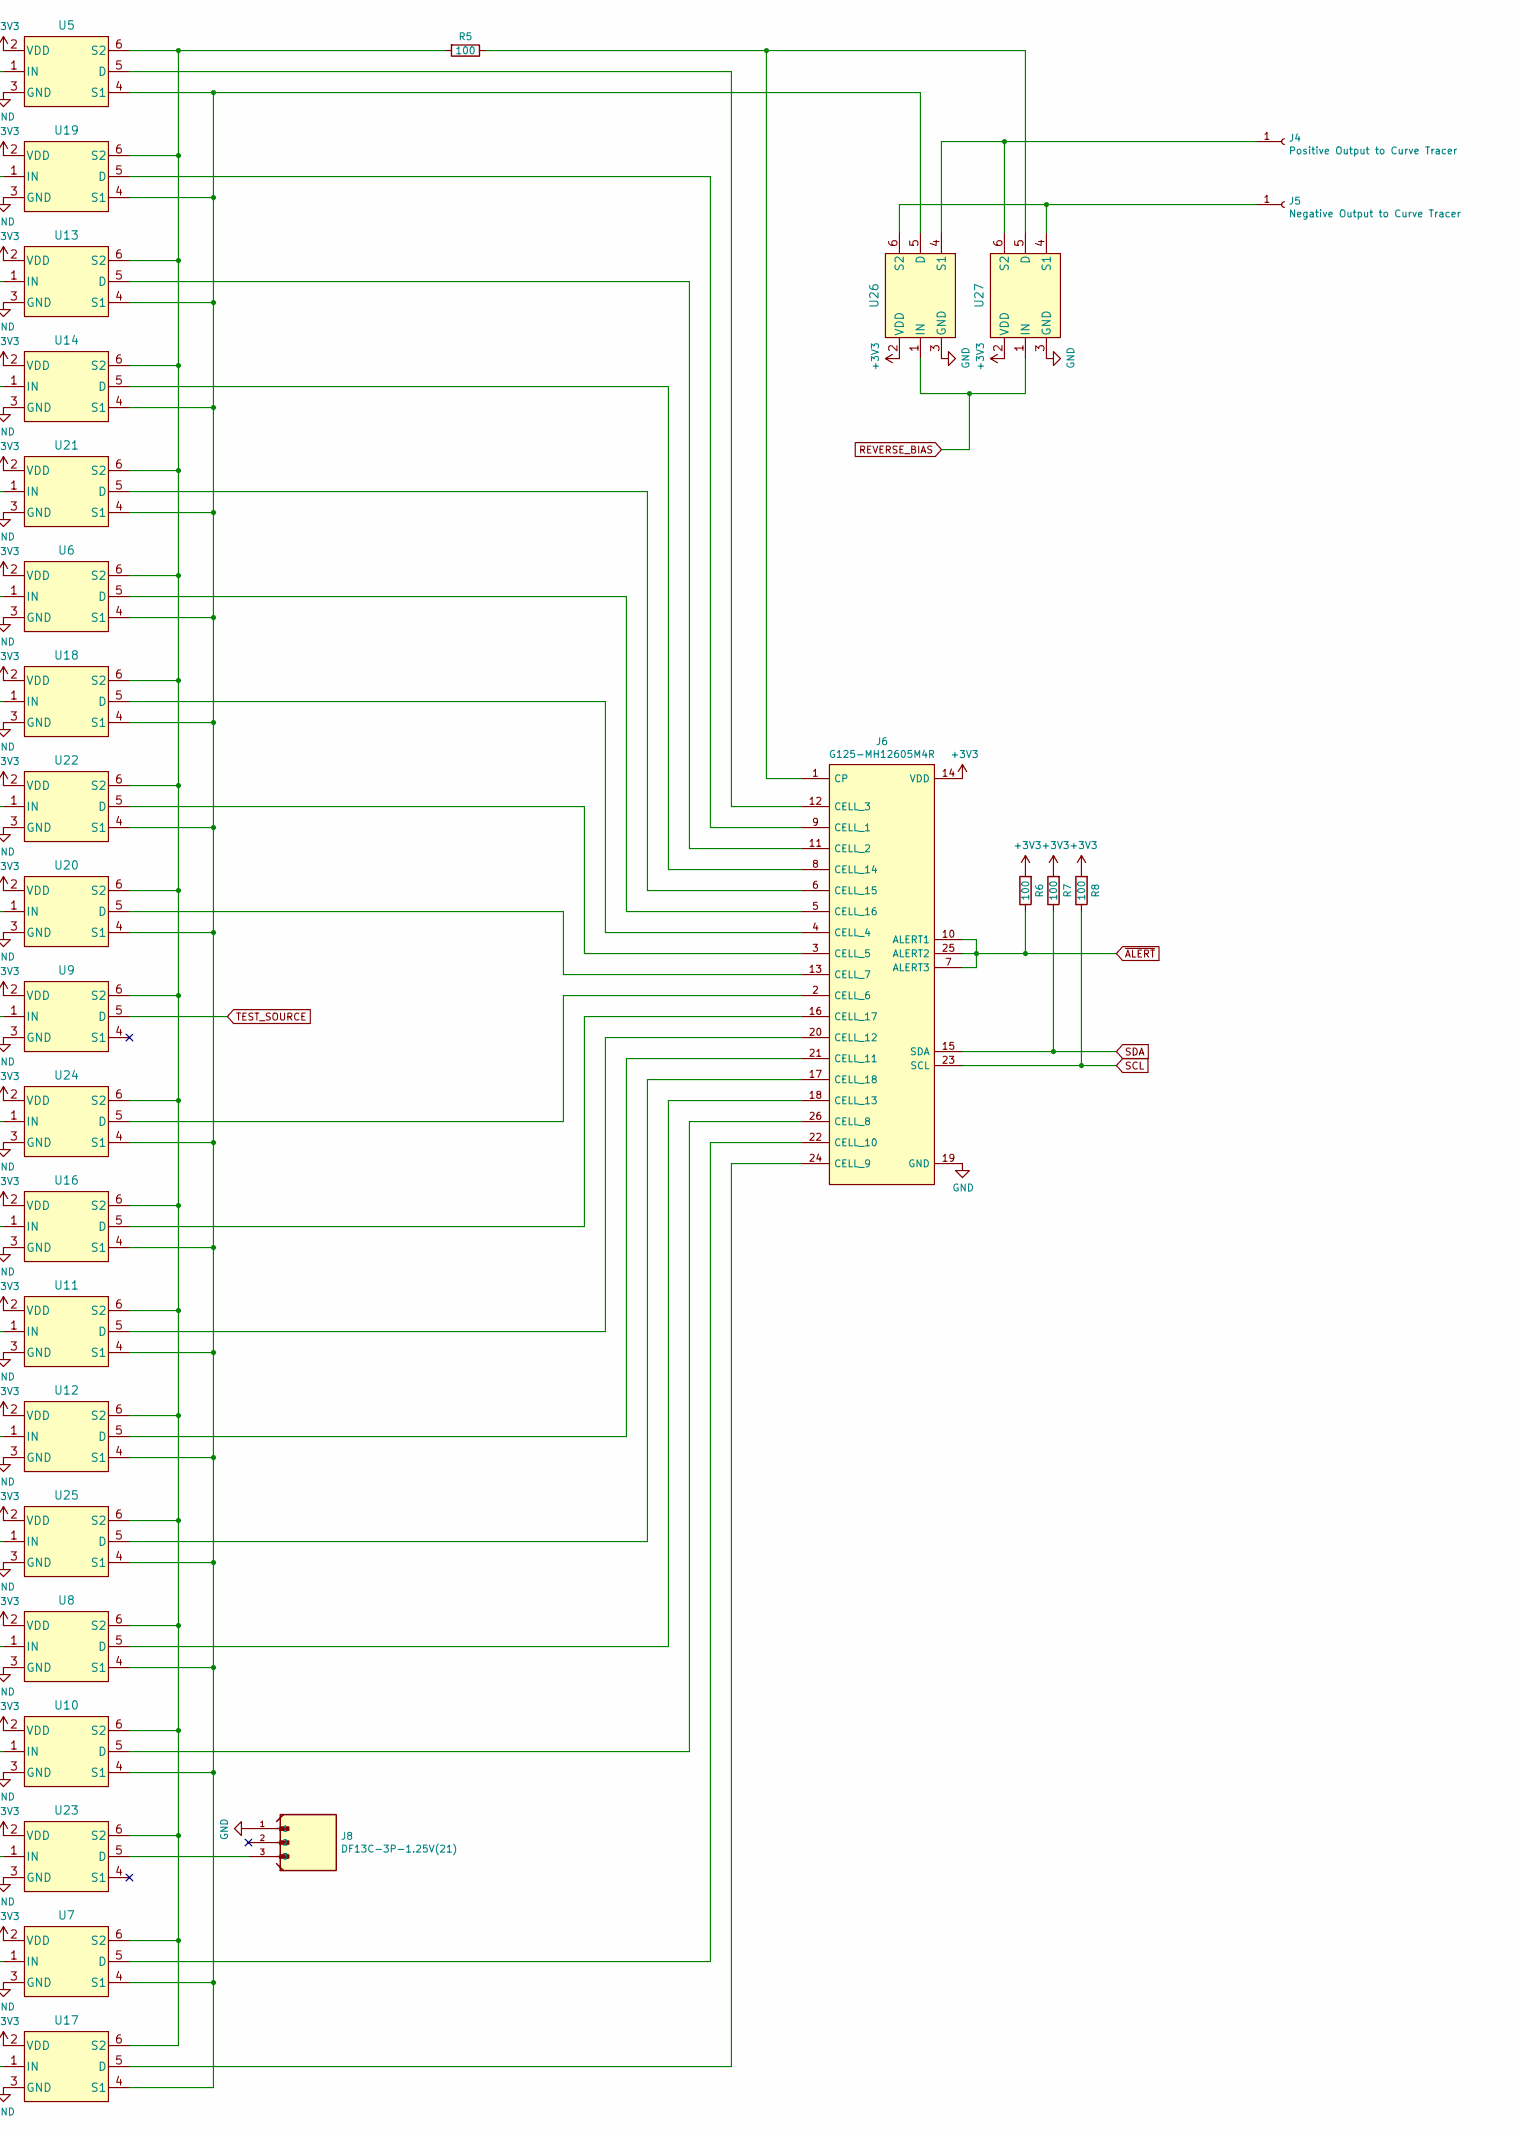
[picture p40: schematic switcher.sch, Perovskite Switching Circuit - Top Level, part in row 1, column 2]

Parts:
C1, C2, C3, C4, C5, C6, C7, C8, C9, C10, C11, C12, C13, C14, C15, C16, C17, C18, C19, C20, C21, C22, C23, C24, C25, C26, C27: 0.1u; C_0603_1608Metric
FB1: Ferrite_Bead; L_0603_1608Metric
J1, J2: Conn_01x10_Female; PinHeader_1x10_P2.54mm_Vertical
J3: Conn_01x12_Female
J4: Positive Output to Curve Tracer; PinHeader_1x01_P2.54mm_Vertical
J5: Negative Output to Curve Tracer; PinHeader_1x01_P2.54mm_Vertical
J6: G125-MH12605M4R; Manufacturer_Part_Number G125-MH12605M4R; Mouser Part Number 855-G125MH1265M4RM4R
J7, J8: DF13C-3P-1.25V(21); HRS_DF13C-3P-1.25V(21)
Q1: DMC2053UVT; TSOT-23-6
R1: 1k; R_0603_1608Metric
R2, R3: 10k; R_0603_1608Metric
R4, R5, R6, R7, R8, R9, R25, R27, R28, R29, R30: 100; R_0603_1608Metric
R24: 20k; R_0603_1608Metric
R26: 1; R_0603_1608Metric
U1: SN74LVC1G14DRL; SOT-23-5
U2: CD4518BM96
U3, U4: CD4514BM
U5, U6, U7, U8, U9, U10, U11, U12, U13, U14, U16, U17, U18, U19, U20, U21, U22, U23, U24, U25, U26, U27: ADG839YKSZ-REEL7
U15: LT3092ETS8TRPBF; TSOT-23_TS8; MANUFACTURER_PART_NUMBER lt3092ets8#trpbf

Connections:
0-9_CLOCK: R25.1, U2.1 (CLOCKA), U4.1 (STROBE)
10-19_CLOCK: R28.1, U2.9 (CLOCKB), U3.1 (STROBE)
+3V3: C1.1, C2.1, C3.1, C4.1, C5.1, C6.1, C7.1, C8.1, C9.1, C10.1, C11.1, C12.1, C13.1, C14.1, C15.1, C16.1, C17.1, C18.1, C19.1, C20.1, C21.1, C22.1, C23.1, C24.1, C25.1, C27.1, FB1.1, J6.14 (VDD), J7.2, Q1.2 (S), R3.1, R6.2, R7.2, R8.2, U1.5 (VCC), U2.16 (VDD), U3.24 (VDD), U4.24 (VDD), U5.2 (VDD), U6.2 (VDD), U7.2 (VDD), U8.2 (VDD), U9.2 (VDD), U10.2 (VDD), U11.2 (VDD), U12.2 (VDD), U13.2 (VDD), U14.2 (VDD), U16.2 (VDD), U17.2 (VDD), U18.2 (VDD), U19.2 (VDD), U20.2 (VDD), U21.2 (VDD), U22.2 (VDD), U23.2 (VDD), U24.2 (VDD), U25.2 (VDD), U26.2 (VDD), U27.2 (VDD)
ENABLE_PANEL_SWITCH: R27.1, U1.2, U2.10 (ENABLEB), U4.23 (INHIBIT)
ENABLE_TEST_SOURCE: R1.2, R29.1
GND: C1.2, C2.2, C3.2, C4.2, C5.2, C6.2, C7.2, C8.2, C9.2, C10.2, C11.2, C12.2, C13.2, C14.2, C15.2, C16.2, C17.2, C18.2, C19.2, C20.2, C21.2, C22.2, C23.2, C24.2, C25.2, C26.1, C27.2, J2.10, J6.19 (GND), J8.1, Q1.5 (S), R2.2, U1.3 (GND), U2.8 (VSS), U3.12 (VSS), U4.12 (VSS), U5.3 (GND), U6.3 (GND), U7.3 (GND), U8.3 (GND), U9.3 (GND), U10.3 (GND), U11.3 (GND), U12.3 (GND), U13.3 (GND), U14.3 (GND), U16.3 (GND), U17.3 (GND), U18.3 (GND), U19.3 (GND), U20.3 (GND), U21.3 (GND), U22.3 (GND), U23.3 (GND), U24.3 (GND), U25.3 (GND), U26.3 (GND), U27.3 (GND)
unnamed: C26.2, Q1.4 (D), U15.7 (IN_2), U15.8 (IN)
unnamed: FB1.2, J1.1
unnamed: J1.2, J7.3
unnamed: J1.5, R29.2
unnamed: J1.6, R30.1
unnamed: J2.1, R4.2
unnamed: J2.2, R9.2
unnamed: J2.3, R25.2
unnamed: J2.4, R28.2
unnamed: J2.5, R27.2
unnamed: J3.1, U4.11 (S0)
unnamed: J3.2, U4.9 (S1)
unnamed: J3.3, U4.10 (S2)
unnamed: J3.4, U4.8 (S3)
unnamed: J3.5, U4.7 (S4)
unnamed: J3.6, U4.6 (S5)
unnamed: J3.7, U3.20 (S10)
unnamed: J3.8, U3.19 (S11)
unnamed: J3.9, U3.14 (S12)
unnamed: J3.10, U3.13 (S13)
unnamed: J3.11, U3.16 (S14)
unnamed: J3.12, U3.15 (S15)
unnamed: J4.1, U26.4 (S1), U27.6 (S2)
unnamed: J5.1, U26.6 (S2), U27.4 (S1)
unnamed: J6.1 (CP), R5.1, U27.5 (D)
unnamed: J6.2 (CELL_6), U24.5 (D)
unnamed: J6.3 (CELL_5), U22.5 (D)
unnamed: J6.4 (CELL_4), U18.5 (D)
unnamed: J6.5 (CELL_16), U6.5 (D)
unnamed: J6.6 (CELL_15), U21.5 (D)
unnamed: J6.8 (CELL_14), U14.5 (D)
unnamed: J6.9 (CELL_1), U19.5 (D)
unnamed: J6.11 (CELL_2), U13.5 (D)
unnamed: J6.12 (CELL_3), U5.5 (D)
unnamed: J6.13 (CELL_7), U20.5 (D)
unnamed: J6.16 (CELL_17), U16.5 (D)
unnamed: J6.17 (CELL_18), U25.5 (D)
unnamed: J6.18 (CELL_13), U8.5 (D)
unnamed: J6.20 (CELL_12), U11.5 (D)
unnamed: J6.21 (CELL_11), U12.5 (D)
unnamed: J6.22 (CELL_10), U7.5 (D)
unnamed: J6.24 (CELL_9), U17.5 (D)
unnamed: J6.26 (CELL_8), U10.5 (D)
unnamed: J8.3, U23.5 (D)
unnamed: Q1.1 (G), R1.1, R2.1
unnamed: Q1.3 (G), Q1.6 (D), R3.2
unnamed: R5.2, U5.6 (S2), U6.6 (S2), U7.6 (S2), U8.6 (S2), U9.6 (S2), U10.6 (S2), U11.6 (S2), U12.6 (S2), U13.6 (S2), U14.6 (S2), U16.6 (S2), U17.6 (S2), U18.6 (S2), U19.6 (S2), U20.6 (S2), U21.6 (S2), U22.6 (S2), U23.6 (S2), U24.6 (S2), U25.6 (S2)
unnamed: R24.2, U15.5 (SET)
unnamed: R26.2, U15.2 (OUT_2), U15.3 (OUT_3), U15.4 (OUT)
unnamed: U2.3 (Q1A), U4.2 (DATA1)
unnamed: U2.4 (Q2A), U4.3 (DATA2)
unnamed: U2.5 (Q3A), U4.21 (DATA3)
unnamed: U2.6 (Q4A), U4.22 (DATA4)
unnamed: U2.11 (Q1B), U3.2 (DATA1)
unnamed: U2.12 (Q2B), U3.3 (DATA2)
unnamed: U2.13 (Q3B), U3.21 (DATA3)
unnamed: U2.14 (Q4B), U3.22 (DATA4)
unnamed: U3.6 (S5), U6.1 (IN)
unnamed: U3.11 (S0), U5.1 (IN)
unnamed: U3.17 (S9), U9.1 (IN)
unnamed: U4.16 (S14), U7.1 (IN)
unnamed: U4.19 (S11), U8.1 (IN)
unnamed: U4.14 (S12), U10.1 (IN)
unnamed: U5.4 (S1), U6.4 (S1), U7.4 (S1), U8.4 (S1), U10.4 (S1), U11.4 (S1), U12.4 (S1), U13.4 (S1), U14.4 (S1), U16.4 (S1), U17.4 (S1), U18.4 (S1), U19.4 (S1), U20.4 (S1), U21.4 (S1), U22.4 (S1), U24.4 (S1), U25.4 (S1), U26.5 (D)
unnamed: U4.18 (S8), U11.1 (IN)
unnamed: U4.17 (S9), U12.1 (IN)
unnamed: U3.10 (S2), U13.1 (IN)
unnamed: U3.8 (S3), U14.1 (IN)
unnamed: U4.4 (S7), U16.1 (IN)
unnamed: U4.15 (S15), U17.1 (IN)
unnamed: U3.5 (S6), U18.1 (IN)
unnamed: U3.9 (S1), U19.1 (IN)
unnamed: U3.18 (S8), U20.1 (IN)
unnamed: U3.7 (S4), U21.1 (IN)
unnamed: U3.4 (S7), U22.1 (IN)
unnamed: U4.13 (S13), U23.1 (IN)
unnamed: U4.5 (S6), U24.1 (IN)
unnamed: U4.20 (S10), U25.1 (IN)
RESET_PANEL_SWITCH: R30.2, U2.7 (RESETA), U2.15 (RESETB)
REVERSE_BIAS: R9.1, U26.1 (IN), U27.1 (IN)
SCL: J1.9, J6.23 (SCL), R8.1
SDA: J1.10, J6.15 (SDA), R7.1
TEST_SOURCE: R24.1, R26.1, U9.5 (D)
~ALERT: J6.7 (ALERT3), J6.10 (ALERT1), J6.25 (ALERT2), R4.1, R6.1
~ENABLE_PANEL_SWITCH: U1.4, U2.2 (ENABLEA), U3.23 (INHIBIT)



Board: 2 copper layers, 69.7 x 61.8 mm, 79 parts (2 on the bottom side), 79 nets.

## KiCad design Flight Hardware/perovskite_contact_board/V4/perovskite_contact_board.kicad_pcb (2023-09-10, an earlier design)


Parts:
C1, C2, C3, C4, C5: 0.1u; C_0603_1608Metric
JP100.1, JP100.2, JP100.3, JP100.4, JP100.5, JP100.6, JP100.7, JP101.1, JP101.2, JP101.3, JP101.4, JP101.5, JP101.6, JP101.7, JP102.1, JP102.2, JP102.3, JP102.4, JP102.5, JP102.6, JP102.7, JP103.1, JP103.2, JP103.3, JP103.4, JP103.5, JP103.6, JP103.7, JP103.8, JP103.9, JP103.10, JP103.11, JP103.12: Conn_01x01; TestPoint_Pad_D2.0mm
U1, U2, U3: Perovskite_CP_6_Cell; Perovskite
U4, U5, U6: MCP9808_MSOP; MCP9804_With_Hole
U7: BME280; Bosch_LGA-8_2.5x2.5mm_P0.65mm_ClockwisePinNumbering

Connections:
CELL_1: JP100.1.1, U1.1 (Cell_1)
CELL_2: JP100.2.1, U1.2 (Cell_2)
CELL_3: JP100.3.1, U1.3 (Cell_3)
CELL_4: JP100.4.1, U1.4 (Cell_4)
CELL_5: JP100.5.1, U1.5 (Cell_5)
CELL_6: JP100.6.1, U1.6 (Cell_6)
CELL_7: JP101.1.1, U2.1 (Cell_1)
CELL_8: JP101.2.1, U2.2 (Cell_2)
CELL_9: JP101.3.1, U2.3 (Cell_3)
CELL_10: JP101.4.1, U2.4 (Cell_4)
CELL_11: JP101.5.1, U2.5 (Cell_5)
CELL_12: JP101.6.1, U2.6 (Cell_6)
CELL_13: JP102.1.1, U3.1 (Cell_1)
CELL_14: JP102.2.1, U3.2 (Cell_2)
CELL_15: JP102.3.1, U3.3 (Cell_3)
CELL_16: JP102.4.1, U3.4 (Cell_4)
CELL_17: JP102.5.1, U3.5 (Cell_5)
CELL_18: JP102.6.1, U3.6 (Cell_6)
CP_1: JP100.7.1, U1.7 (Common_Positive)
CP_2: JP101.7.1, U2.7 (Common_Positive)
CP_3: JP102.7.1, U3.7 (Common_Positive)
GND: C1.2, C2.2, C3.2, C4.2, C5.2, JP103.1.1, JP103.5.1, JP103.9.1, U4.4 (GND), U4.5 (A2), U4.6 (A1), U5.4 (GND), U5.5 (A2), U6.4 (GND), U7.1 (GND), U7.7 (GND)
SCL1: JP103.3.1, U4.2 (SCL)
SCL2: JP103.7.1, U5.2 (SCL)
SCL3: JP103.11.1, U6.2 (SCL), U7.4 (SCK)
SDA1: JP103.4.1, U4.1 (SDA)
SDA2: JP103.8.1, U5.1 (SDA), U7.3 (SDI)
SDA3: JP103.12.1, U6.1 (SDA)
VDD: C1.1, C2.1, C3.1, JP103.2.1, U4.7 (A0), U4.8 (VDD), U7.2 (CSB), U7.5 (SDO), U7.6 (VDDIO), U7.8 (VDD)
VDDA: C4.1, JP103.6.1, U5.6 (A1), U5.7 (A0), U5.8 (VDD)
VDDF: C5.1, JP103.10.1, U6.5 (A2), U6.6 (A1), U6.7 (A0), U6.8 (VDD)



Board: 2 copper layers, 55.2 x 55.2 mm, 45 parts (42 on the bottom side), 31 nets.

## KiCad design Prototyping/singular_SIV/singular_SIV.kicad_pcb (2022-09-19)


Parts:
C1: C; C_1206_3216Metric
DP1: AD8400; AD8400 DP
J1: Conn_01x02; PinHeader_1x02_P2.54mm_Vertical
J2: Conn_01x05; JST_XH_B5B-XH-A_1x05_P2.50mm_Vertical
O1: INA4180; SOP65P640X120-14N
R1: R; R_1206_3216Metric
U1: Teensy4.1; Teensy41

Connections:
5V: J2.1, J2.5, U1.48 (VIN)
A0: J1.2, O1.3 (IN+1), R1.1, U1.36 (14_A0_TX3_SPDIF_OUT)
A1: O1.1 (OUT1), U1.37 (15_A1_RX3_SPDIF_IN)
CS: DP1.3 (~CS), U1.12 (10_CS_MQSR)
GND: C1.2, DP1.2 (GND), DP1.7 (W1), J1.1, J2.2, J2.4, O1.11 (GND), U1.1 (GND)
MOSI: DP1.4 (SDI), U1.13 (11_MOSI_CTX1)
unnamed: DP1.8 (A1), O1.2 (IN-1), R1.2
SCK: DP1.5 (CLK), U1.35 (13_SCK_LED)
VDD: C1.1, DP1.6 (VDD), O1.4 (VS), U1.46 (3V3)


Board: 2 copper layers, 22.3 x 89.4 mm, 7 parts (0 on the bottom side), 9 nets.

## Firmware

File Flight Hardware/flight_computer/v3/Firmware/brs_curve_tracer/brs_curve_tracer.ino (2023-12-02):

#include "Energia.h"
#include "FSS100.h"
#include <MCP9808.h>
#include <OneWire.h>
#include <stdio.h>
#include "NSL_EPS.h"
#include <Wire.h>
#include <MLX90393.h>
#include <TinyBME280.h>
#include <ICM20649.h>

#define DEBUGGING
#define NO_TRANSMIT

#define COUNT_UP HIGH
#define COUNT_DOWN LOW

#define MUX_POS_GAAS 0
#define MUX_POS_P1 3
#define MUX_POS_P2 2
#define MUX_POS_P3 1

#define PEROVSKITE_1_LOWER    0b001
#define PEROVSKITE_2_LOWER    0b010
#define PEROVSKITE_3_LOWER    0b100

#define SETTLING_TIME 10

#define MAX_PIXELS 6
#define MAX_LADDER_STEPS 16
#define EPS_SEND_TIMEOUT -1

// Cutoff voltage set to 6.5V
#define BUSS_VOLTAGE_CUTOFF 0x7E
uint8_t battery_voltage;

byte pixel_packet_1[] = {0x50, 0x50, 0x50, 0x0C, 0x00, 0x00, 0x00, 0x00, 0x00, 0x00, 0x00, 0x00, 0x00, 0x00, 0x00, 0x00, 0x00, 0x00, 0x00, 0x00, 0x00};
byte pixel_packet_2[] = {0x50, 0x50, 0x50, 0x0C, 0x00, 0x00, 0x00, 0x00, 0x00, 0x00, 0x00, 0x00, 0x00, 0x00, 0x00, 0x00, 0x00, 0x00, 0x00, 0x00, 0x00};
byte pixel_packet_3[] = {0x50, 0x50, 0x50, 0x0C, 0x00, 0x00, 0x00, 0x00, 0x00, 0x00, 0x00, 0x00, 0x00, 0x00, 0x00, 0x00, 0x00, 0x00, 0x00, 0x00, 0x00};
byte pixel_packet_4[] = {0x50, 0x50, 0x50, 0x0C, 0x00, 0x00, 0x00, 0x00, 0x00, 0x00, 0x00, 0x00, 0x00, 0x00, 0x00, 0x00, 0x00, 0x00, 0x00, 0x00, 0x00};

byte flux_packet_1[] = {0x50, 0x50, 0x50, 0x0C, 0x00, 0x00, 0x00, 0x00, 0x00, 0x00, 0x00, 0x00, 0x00, 0x00, 0x00, 0x00, 0x00, 0x00, 0x00, 0x00, 0x00};
byte flux_packet_2[] = {0x50, 0x50, 0x50, 0x0C, 0x00, 0x00, 0x00, 0x00, 0x00, 0x00, 0x00, 0x00, 0x00, 0x00, 0x00, 0x00, 0x00, 0x00, 0x00, 0x00, 0x00};
byte flux_packet_3[] = {0x50, 0x50, 0x50, 0x0C, 0x00, 0x00, 0x00, 0x00, 0x00, 0x00, 0x00, 0x00, 0x00, 0x00, 0x00, 0x00, 0x00, 0x00, 0x00, 0x00, 0x00};
byte flux_packet_4[] = {0x50, 0x50, 0x50, 0x0C, 0x00, 0x00, 0x00, 0x00, 0x00, 0x00, 0x00, 0x00, 0x00, 0x00, 0x00, 0x00, 0x00, 0x00, 0x00, 0x00, 0x00};

byte secondary_packet[] = {0x50, 0x50, 0x50, 0x0C, 0x00, 0x00, 0x00, 0x00, 0x00, 0x00, 0x00, 0x00, 0x00, 0x00, 0x00, 0x00, 0x00, 0x00, 0x00, 0x00, 0x00};
byte tertiary_packet[] = {0x50, 0x50, 0x50, 0x0C, 0x00, 0x00, 0x00, 0x00, 0x00, 0x00, 0x00, 0x00, 0x00, 0x00, 0x00, 0x00, 0x00, 0x00, 0x00, 0x00, 0x00};

byte status_register = 0x00;

byte shutdown_payload[] = {0x50, 0x50, 0x50, 0x0B, 0x00, 0x00, 0x00, 0x00, 0x00, 0x00, 0x00, 0x00, 0x00, 0x00, 0x00, 0x00, 0x00, 0x00, 0x00, 0x00, 0x00};
byte heartbeat_payload[] = {0x50, 0x50, 0x50, 0x0B, 0xFF, 0xFF, 0xFF, 0xFF, 0xFF, 0xFF, 0xFF, 0x00, 0x00, 0x00, 0x00, 0x00, 0x00, 0x00, 0x00, 0x00, 0x00};

uint16_t flux[16] = { 0 };
uint16_t current_1[16] = { 0 };
uint16_t voltage_1[16] = { 0 };
uint16_t current_2[16] = { 0 };
uint16_t voltage_2[16] = { 0 };
uint16_t current_3[16] = { 0 };
uint16_t voltage_3[16] = { 0 };
uint16_t current_4[16] = { 0 };
uint16_t voltage_4[16] = { 0 };

int i, mp_1, mp_1i, mp_2, mp_2i, mp_3, mp_3i, mp_4, mp_4i;

#define STATUS_REGISTER_PIXEL_BIT_0   0
#define STATUS_REGISTER_PIXEL_BIT_1   1
#define STATUS_REGISTER_PIXEL_BIT_2   2
#define STATUS_REGISTER_SAMPLE_BIT_0  3
#define STATUS_REGISTER_SAMPLE_BIT_1  4
#define STATUS_REGISTER_PACKET_BIT_0  5
#define STATUS_REGISTER_PACKET_BIT_1  6
#define STATUS_REGISTER_DIRECTION_BIT  7

// Temperature sensors on the payload
MCP9808 perovskite_1(PEROVSKITE_1_LOWER);
MCP9808 perovskite_2(PEROVSKITE_2_LOWER);
MCP9808 perovskite_3(PEROVSKITE_3_LOWER);

EPS eps(EPS_RX, EPS_TX);

MLX90393 magnetometer(0x18);
MLX90393::txyzRaw mag_data;
ICM20649 imu;

// Temperature sensor on the reference GaAs panel
OneWire gaas_temp_sensor(GAAS_TEMP);
// Sun vector sensor
FSS100 sun_sensor(0x57);

volatile int current_rot = 0;
int16_t theta;
int16_t phi;
uint8_t current_pixel = 0;
uint32_t humidity_reading = 0;
uint32_t pressure_reading = 0;
uint16_t p_1_temperature;
uint16_t p_2_temperature;
uint16_t p_3_temperature;
uint16_t gaas_temperature;
volatile bool trace_dir;

///////////////////////////////////////////
//       START PRIMARY PAYLOAD CODE
///////////////////////////////////////////

bool read_gaas_temp(uint16_t *gaas_temp_reading)
{
  byte i;
  byte present = 0;
  byte type_s;
  byte data[9];
  byte addr[8];

  if (!gaas_temp_sensor.search(addr)) {
    gaas_temp_sensor.reset_search();
    return false;
  }

  if (OneWire::crc8(addr, 7) != addr[7]) {
    return false;
  }

  // the first ROM byte indicates which chip
  switch (addr[0]) {
    case 0x10:
      type_s = 1;
      break;
    case 0x28:
      type_s = 0;
      break;
    case 0x22:
      type_s = 0;
      break;
    default:
      return false;
  }

  gaas_temp_sensor.reset();
  gaas_temp_sensor.select(addr);
  gaas_temp_sensor.write(0x44, 1);        // start conversion, with parasite power on at the end

  delay(1000);     // maybe 750ms is enough, maybe not
  // we might do a ds.depower() here, but the reset will take care of it.

  present = gaas_temp_sensor.reset();
  gaas_temp_sensor.select(addr);
  gaas_temp_sensor.write(0xBE);         // Read Scratchpad

  for ( i = 0; i < 9; i++) {           // we need 9 bytes
    data[i] = gaas_temp_sensor.read();
  }
  gaas_temp_sensor.depower();

  // Convert the data to actual temperature
  // because the result is a 16 bit signed integer, it should
  // be stored to an "int16_t" type, which is always 16 bits
  // even when compiled on a 32 bit processor.
  int16_t raw = (data[1] << 8) | data[0];
  if (type_s) {
    raw = raw << 3; // 9 bit resolution default
    if (data[7] == 0x10) {
      // "count remain" gives full 12 bit resolution
      raw = (raw & 0xFFF0) + 12 - data[6];
    }
  } else {
    byte cfg = (data[4] & 0x60);
    // at lower res, the low bits are undefined, so let's zero them
    if (cfg == 0x00) raw = raw & ~7;  // 9 bit resolution, 93.75 ms
    else if (cfg == 0x20) raw = raw & ~3; // 10 bit res, 187.5 ms
    else if (cfg == 0x40) raw = raw & ~1; // 11 bit res, 375 ms
    //// default is 12 bit resolution, 750 ms conversion time
  }
  *gaas_temp_reading = raw;
  return true;
}

#define ROTATION_END 5
volatile long last_p3_time = 0;
volatile bool last_p3_en = false;
volatile long center_time = 0;
volatile long rotation = 0;
volatile uint8_t trigger_current = 0;

void p3_rotation_isr(void)
{
  //__bic_SR_register_on_exit(LPM4_bits);
  if (!last_p3_en)
  {
    if (last_p3_time != 0)
    {
      rotation = millis() - last_p3_time;
    }
    last_p3_time = millis();
    last_p3_en = true;
  }
}

// Do we need center time? Could probably skip and just wait.
// Nope need it
# define CENTER_TIME
void p3_wait(void)
{
  trigger_current = analogRead(PANEL_3_CURRENT_V);
  detachInterrupt(digitalPinToInterrupt(PANEL_3_ON));
#ifdef CENTER_TIME
  uint8_t max_current = 0;
  long max_current_time = 0;
  uint8_t zero_checks = ROTATION_END;
  while (zero_checks != 0)
  {
    uint8_t panel_current = analogRead(PANEL_3_CURRENT_V);
    long panel_current_time = millis();
    if (panel_current != 0)
    {
      if (panel_current + 50 > trigger_current)
      {
        max_current = panel_current;
        max_current_time = panel_current_time;
        zero_checks = ROTATION_END;
      }
      else
      {
        zero_checks--;
      }
    }
  }
  center_time = max_current_time - last_p3_time;
  if (center_time > 0 && rotation > 1000) delay((uint16_t)((rotation / 2) + center_time));
#else
  delay(rotation / 2);
#endif
  attachInterrupt(digitalPinToInterrupt(PANEL_3_ON), p3_rotation_isr, RISING);
  last_p3_en = false;
}

uint8_t init_payload(void)
{
  uint8_t all_status = 0;
  uint8_t status = perovskite_1.begin();
  if (status != 0) all_status |= (1 << 0);
  status = perovskite_2.begin();
  if (status != 0) all_status |= (1 << 1);
  status = perovskite_3.begin();
  if (status != 0) all_status |= (1 << 2);
  BME280setup();
  return all_status;
}

void read_payload(uint16_t *p_1, uint16_t *p_2, uint16_t *p_3)
{
  *p_1 = perovskite_1.read_ambient();
  *p_2 = perovskite_2.read_ambient();
  *p_3 = perovskite_3.read_ambient();
}

void read_bme280(void)
{
  humidity_reading = BME280humidity();
  pressure_reading = BME280pressure();
}

///////////////////////////////////////////
//       END PRIMARY PAYLOAD CODE
///////////////////////////////////////////

///////////////////////////////////////////
//       START CURVE TRACER CODE
///////////////////////////////////////////

byte ladder_step = 0;

void step_ladder(void)
{
  digitalWrite(LADDER_CLOCK, LOW);
  digitalWrite(LADDER_CLOCK, HIGH);
  ladder_step++;
}

void reset_ladder(void)
{
  while (digitalRead(CT_GOOD)) 
  {
    step_ladder(); // Set the ladder to 0xF
    delay(10);
  }
  if (trace_dir == COUNT_UP) step_ladder(); // Set the ladder to 0x0
  ladder_step = 0;
}

void reset_mux(void)
{
  digitalWrite(MUX_RESET, HIGH);
  digitalWrite(MUX_RESET, LOW);
  current_pixel = 0;
}

void step_mux(void)
{
  digitalWrite(MUX_CLOCK, HIGH);
  digitalWrite(MUX_CLOCK, LOW);
  current_pixel++;
}

void set_trace_direction(uint8_t dir)
{
  if (dir == COUNT_UP)
  {
    digitalWrite(TRACE_DIR, COUNT_UP);
    trace_dir = COUNT_UP;
  }
  else
  {
    digitalWrite(TRACE_DIR, COUNT_DOWN);
    trace_dir = COUNT_DOWN;
  }
}

void set_read_mux(uint8_t mux_pos)
{
  switch (mux_pos)
  {
    case MUX_POS_GAAS:
#ifdef DEBUGGING
      //      Serial.println("Setting analog mux to GaAs position");
#endif
      digitalWrite(S0_CT, LOW);
      digitalWrite(S1_CT, LOW);
      break;
    case MUX_POS_P1:
#ifdef DEBUGGING
      //      Serial.println("Setting analog mux to P1 position");
#endif
      digitalWrite(S0_CT, HIGH);
      digitalWrite(S1_CT, LOW);
      break;
    case MUX_POS_P2:
#ifdef DEBUGGING
      //      Serial.println("Setting analog mux to P2 position");
#endif
      digitalWrite(S0_CT, LOW);
      digitalWrite(S1_CT, HIGH);
      break;
    case MUX_POS_P3:
#ifdef DEBUGGING
      //      Serial.println("Setting analog mux to P3 position");
#endif
      digitalWrite(S0_CT, HIGH);
      digitalWrite(S1_CT, HIGH);
      break;
    default:
#ifdef DEBUGGING
      //      Serial.println("Setting analog mux to undefined position");
#endif
      break;
  }
}

void read_mux(uint16_t *voltage, uint16_t *current)
{
  *voltage = analogRead(READ_VOLTAGE);
  *current = analogRead(READ_CURRENT);
#ifdef DEBUGGING
  //  Serial.print("V: "); Serial.print(*voltage); Serial.print(" | I: "); Serial.println(*current);
#endif
}

///////////////////////////////////////////
//       END CURVE TRACER CODE
///////////////////////////////////////////

///////////////////////////////////////////
//       START SECONDARY PAYLOAD CODE
///////////////////////////////////////////

volatile long start_time, end_time;
uint16_t nc_time, no_time;
volatile bool relay_done = false;
bool relay_selector = false;

#pragma vector = COMP_E_VECTOR
__interrupt void COMPE_ISR(void)
{
  relay_done = true;
  end_time = micros();
  //Serial.println("COMPE ISR");
  //  if((CECTL2 & CEOUT)==0x01)
  //  {
  //
  //  }
}

void set_relay_comparator (int pin)
{
  Serial.print(CECTL1, BIN);
  Serial.print(" | ");
  Serial.print(CECTL2, BIN);
  Serial.print(" | ");
  Serial.print(CEINT, BIN);
  Serial.println(" | ");
  CECTL0 = CEIPSEL_12;  // P1.1 = +comp
  //  CEINT |= CEIE;
  CECTL1 = CERSEL + CEREFL_2 + CEON;
  Serial.print(CECTL1, BIN);
  Serial.print(" | ");
  Serial.print(CECTL2, BIN);
  Serial.print(" | ");
  Serial.print(CEINT, BIN);
  Serial.println(" | ");
}
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

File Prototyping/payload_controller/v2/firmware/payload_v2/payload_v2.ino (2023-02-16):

/*
 * Payload Controller Firmware
 * UNL Aerospace Club
 * Aerospace eXperimental Payloads
 * 
 * Author: Walker Arce
 * Date: 26 Dec 2022
 */
#include "ADS131M04.h"
#include <MCP9808.h>      // http://github.com/JChristensen/MCP9808
#include "MCP4725.h"
#include <OneWire.h> 

// ADC Pins
#define ADC_CS    11
#define ADC_DRDY  18
#define ADC_MOSI  15
#define ADC_MISO  14
#define ADC_SCLK  7
#define ADC_SYNC  6
#define ADC_CLK   5

#define R_DIVIDER_V       A7
#define R_DIVIDER_I       A11

// Perovskite Multiplexer Pins
#define ENABLE_TEST_SOURCE    2
#define RESET_PANEL_SWITCH_A    27
#define RESET_PANEL_SWITCH_B  ADC_CS
#define ENABLE_PANEL_SWITCH   22
#define DECODER_10_19_CLOCK   21
#define DECODER_0_9_CLOCK     25

// Resistor Ladder Pins
#define R_DIVIDER_CLOCK   12
#define R_DIVIDER_LATCH   28
#define R_DIVIDER_RESET   13
#define R_DIVIDER_ENABLE  19

// GaAs Panel Pins
#define GAAS_TEMP A9

// Other Pins
#define FAULT         8
#define REVERSE_BIAS  26
#define ALERT         23

// Process Control Variables
#define ANALOG_SAMPLES_V      5
#define ANALOG_SAMPLES_I      5
#define DAC_ADDRESS           0x66
#define PEROVSKITE_1_LOWER    1
#define PEROVSKITE_2_LOWER    3 
#define PEROVSKITE_3_LOWER    7
#define FSS100_ADDRESS        0x57


#define ANALOG_SAMPLES_V    5
#define ANALOG_SAMPLES_I    5


ADS131M04 adc;
adcOutput res;

MCP9808 perovskite_1(PEROVSKITE_1_LOWER);
MCP9808 perovskite_2(PEROVSKITE_2_LOWER);
MCP9808 perovskite_3(PEROVSKITE_3_LOWER);

MCP4725 dac(DAC_ADDRESS); 

OneWire ds(GAAS_TEMP);

volatile int current_panel = 0;
volatile int current_step = 0;
volatile uint8_t status_register = 0;
volatile bool reverse_bias = false;

int v_readings[256];
int i_readings[256];

void setup_pins(void)
{
  pinMode(ENABLE_TEST_SOURCE, OUTPUT);
  digitalWrite(ENABLE_TEST_SOURCE, LOW);
  
  pinMode(RESET_PANEL_SWITCH_A, OUTPUT);
  digitalWrite(RESET_PANEL_SWITCH_A, LOW);

  pinMode(RESET_PANEL_SWITCH_B, OUTPUT);
  digitalWrite(RESET_PANEL_SWITCH_B, LOW);
  
  pinMode(ENABLE_PANEL_SWITCH, OUTPUT);
  digitalWrite(ENABLE_PANEL_SWITCH, LOW);
  
  pinMode(DECODER_10_19_CLOCK, OUTPUT);
  digitalWrite(DECODER_10_19_CLOCK, LOW);
  
  pinMode(DECODER_0_9_CLOCK, OUTPUT);
  digitalWrite(DECODER_0_9_CLOCK, LOW);

  pinMode(R_DIVIDER_CLOCK, OUTPUT);
  digitalWrite(R_DIVIDER_CLOCK, LOW);
  
  pinMode(R_DIVIDER_LATCH, OUTPUT);
  digitalWrite(R_DIVIDER_LATCH, HIGH);
  
  pinMode(R_DIVIDER_RESET, OUTPUT);
  pinMode(R_DIVIDER_RESET, HIGH);
  
  pinMode(R_DIVIDER_ENABLE, OUTPUT);
  digitalWrite(R_DIVIDER_ENABLE, LOW);

  pinMode(FAULT, OUTPUT);
  digitalWrite(FAULT, LOW);

  pinMode(REVERSE_BIAS, OUTPUT);
  digitalWrite(REVERSE_BIAS, LOW);

  pinMode(ALERT, INPUT);
  pinMode(R_DIVIDER_V, INPUT);
  pinMode(R_DIVIDER_I, INPUT);
//  pinMode(ADC_SYNC, OUTPUT);
//  digitalWrite(ADC_SYNC, HIGH);
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

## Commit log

2022-09-19 Update board designs
    [AD8400ARZ1.step, ADG841YKSZ-500RL7.STEP, Analog_Power_Supply.sch, Bypass_Caps.sch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]
2022-10-11 Update boards
    - Added flight computer board outline
    - Added GUI for curve tracer
    - Updated curve tracer
    - Updated perovskite switcher
    [Perovskite_Switches.sch, curve_tracer-B_Cu.gbr, curve_tracer-B_Mask.gbr, curve_tracer-B_Paste.gbr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]
2022-11-01 Add curve tracer software and curves
    [curve_0.csv, curve_10_f_313.csv, curve_11.csv, curve_12.csv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]
2022-11-07 these boards may have some problems and may not produce correct step files...
    [G125-MH12605M4R.stp, G125-MV12605M1P.stp, JoelUpdatedPCB.kicad_pcb, JoelUpdatedPCB.kicad_sch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]
2022-11-09 Working on flight computer
    - Update resistor ladder curve tracer silkscreen, schematic, and layout
    - Flight computer schematic drafted for MSP430 circuits, updated curve tracer, perovskite switching network.
    [Analog_Power_Supply.sch, cubesat.sch, curve_tracer-B_Cu.gbr, curve_tracer-B_Mask.gbr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]
2022-11-10 pushing changes from Monday meeting
    [perovskite_contact_board.kicad_pcb, perovskite_contact_board.sch, perovskite_contact_board.step]
2022-11-10 Switched to 0603 package, no longer castillated holes used for the mcp9804, all traces on back layer
    [perovskite_contact_board.kicad_pcb, perovskite_contact_board.sch]
2022-11-12 Updating flight computer
    - Added datasheets for peripherals
    - Added resistor ladder firmware
    - Added perovskite switcher firmware
    - Started flight computer firmware
    - Added curve comparisons
    - Updating flight computer schematic
    [ADS131M04IPWR.step, ICL7660CSAT.step, curve_tracer.sch, flight_computer.sch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]
2022-11-13 Update flight computer schematic
    [curve_tracer.sch, flight_computer.sch, mission_payload.sch, resistor_ladder.sch]
2022-11-14 Annotating schematic with references and footprints
    [CM8V-T1A-32.768KHZ-7PF-20PPM-TA-QC.step, LT3092EDD_TRPBF.step, curve_tracer.sch, fault_watchdog.sch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]
2022-11-17 Contact board update with 2.54 spacing
    [perovskite_contact_board.kicad_pcb, perovskite_contact_board.sch]
2022-11-17 moved headers to fit connection to routing board and switch symbols to proper form
    [Top Plane With connectors.dxf, perovskite_contact_board.kicad_pcb, perovskite_contact_board.sch, perovskite_contact_board.step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]
2022-11-18 new headers added and spacing fixed to allow for 26 pin connector
    [8Pin Version SL-112-T-39 v1.step, SL-112-T-39.stp, Top Plane With connectors.dxf, perovskite_contact_board.kicad_pcb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]
2022-11-18 added mounting holes for bottom PCB
    [TSM-108-01-T-SV.stp, perovskite_contact_board.kicad_pcb, perovskite_contact_board.step, perovskite_routing_board.kicad_pcb]
2022-11-24 Continuing layout
    [0781710004.step, curve_tracer.sch, flight_computer.kicad_pcb, flight_computer.sch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]
2022-11-24 contact board oriented correctly
    [TopPlaneWithConnector11.24.22.dxf, perovskite_contact_board.kicad_pcb, perovskite_contact_board.sch, perovskite_contact_board.step]
2022-11-24 update routing board
    [perovskite_routing_board.kicad_pcb]
2022-11-25 routing board done and nice and pretty
    [perovskite_routing_board.kicad_pcb, perovskite_routing_board.sch]
2022-11-25 added pull up resistor
    [perovskite_routing_board.kicad_pcb, perovskite_routing_board.sch]
2022-11-25 added 3d perovskite
    [Perovskite v2.step, perovskite_contact_board.kicad_pcb, perovskite_contact_board.step]
2022-11-27 Updating designs
    - Generate gerbers
    - Generate renders
    - Working on layout for payload controller
    [0781710004.step, ADS131M04IPWR.step, CD4028BMT.step, CD4072BM.step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]
2022-11-30 Continuing payload design
    - Add OR gate for reverse bias
    - Add GaAs panel connectors
    - Add 3D models
    [SC70-3.iges, SC70-3.step, SC70-4.iges, SC70-4.step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]
2022-11-30 Completed routing
    [CB3LV-3I-8M1920.step, ECS-81.92-12-30Q-EN-TR.step, curve_tracer.sch, flight_computer.kicad_pcb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]
2022-12-01 Generated manufacturing files
    [curve_tracer.sch, flight_computer-B_Cu.gbr, flight_computer-B_Mask.gbr, flight_computer-B_Paste.gbr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]
2022-12-01 Update disconnected trace, regenerate
    - Delete extra projects
    - Package gerbers
    [8Pin Version SL-112-T-39 v1.step, G125-MH12605M4R.stp, G125-MV12605M1P.stp, JoelUpdatedPCB.kicad_pcb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]
2022-12-01 Finalize before order
    [flight_computer-B_Cu.gbr, flight_computer-B_Mask.gbr, flight_computer-B_Paste.gbr, flight_computer-Edge_Cuts.gbr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]
2022-12-03 Add expansion board
    [0781710004.step, 1985014.stp, ADS131M04IPWR.step, CB3LV-3I-8M1920.step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]
2022-12-27 Create payload controller test firmware
    [flight_computer.kicad_pcb]
2023-01-09 Updating boards
    [0781710004.step, ADS131M04IPWR.step, CB3LV-3I-8M1920.step, CD4028BMT.step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]
2023-02-16 fixed backwards connector on routing board
    [perovskite_routing_board-B_Cu.gbr, perovskite_routing_board-B_Mask.gbr, perovskite_routing_board-B_Paste.gbr, perovskite_routing_board-B_SilkS.gbr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]
2023-02-26 Finish updated switcher
    [0781710004.step, CD4028BMT.step, G125-MH12605M4R.stp, G125-MV12605M1P.stp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]
2023-04-03 added Tag Connect folder with KiCad files
    [Tag Connector.kicad_pcb, Tag Connector.sch, Tag Connector.step]
2023-04-25 updated manufacturing files
    used correct dxf file to adjust the mounting holes on the PCB
    [Tag Connector-B_Cu.gbr, Tag Connector-B_Mask.gbr, Tag Connector-B_Paste.gbr, Tag Connector-B_SilkS.gbr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]
2023-07-06 Working on NREL pieces
    [0781710004.step, 1SkiteHolder.DXF, 2-1419130-4.step, ADG841YKSZ-500RL7.STEP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]
2023-07-16 backup v3 contact board
    [outlineV2.dxf, perovskite_contact_board.kicad_pcb, perovskite_contact_board.sch]
2023-07-16 push for review
    [perovskite_contact_board.kicad_pcb]
2023-07-16 updated 3d models
    [perovskite_contact_board.step]
2023-07-19 Update ready for review
    Swapped to circular 2mm touch point pads.
    Updated 3d models.
    Ready for review.
    [assembly.step, perovskite_contact_board.kicad_pcb, perovskite_contact_board.sch, perovskite_contact_board.step]
2023-07-19 updated ground fill plane
    [perovskite_contact_board.kicad_pcb]
2023-07-20 Review contact board
    [0781710004.step, ADS131M04IPWR.step, CB3LV-3I-8M1920.step, CD4028BMT.step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]
2023-07-20 centered vias, added all redundant pads, standardized text
    [perovskite_contact_board.kicad_pcb, perovskite_contact_board.sch, perovskite_contact_board.step]
2023-07-21 isolating nets and fixing silk screen
    [perovskite_contact_board.kicad_pcb, perovskite_contact_board.sch]
2023-07-21 Approve V3 of perovskite contact board
    - Update copyright year and approved line
    - Add NREL tester board firmware
    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
    [perovskite_contact_board-B_Cu.gbr, perovskite_contact_board-B_Mask.gbr, perovskite_contact_board-B_Paste.gbr, perovskite_contact_board-B_SilkS.gbr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]
2023-07-23 Order perovskite contact board
    [perovskite_contact_board-B_Cu.gbr, perovskite_contact_board-B_Mask.gbr, perovskite_contact_board-B_Paste.gbr, perovskite_contact_board-B_SilkS.gbr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]
2023-08-11 fix rotation of perovskites on contact board
    [perovskite_contact_board.kicad_pcb]
2023-08-14 Nearing first pass layout for Rev B flight computer
    [1SkiteHolder.DXF, 530471110.stp, EPS PCB Asm v17.STEP.STEP.step, MCP9801-M_MS.stp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]
2023-08-17 Finished layout of flight computer
    [brs_flight_computer-B_Cu.gbr, brs_flight_computer-B_Mask.gbr, brs_flight_computer-B_Paste.gbr, brs_flight_computer-B_SilkS.gbr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]
2023-08-17 Flight computer v2 complete
    [0781710004.step, 530471110.stp, ADS131M04IPWR.step, CB3LV-3I-8M1920.step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]
2023-08-19 Finishing touches
    - Fill out bill of material
    - Add selection guides
    - Update curve tracer resistors
    - Update finish date
    [flight computer v2 bom.xlsx, resistor_ladder.sch]
2023-08-19 Update flight computer v2 bom.xlsx
    [flight computer v2 bom.xlsx]
2023-08-31 Create v3 flight computer
    [0781710004.step, 530471110.stp, ADS131M04IPWR.step, CB3LV-3I-8M1920.step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]
2023-09-03 Updating based on harnesses
    [brs_flight_computer.kicad_pcb, brs_flight_computer.sch, curve_tracer.sch, eps_connections.sch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]
2023-09-04 Integrating flight computer
    - EPS commands tested and working
    - Updated v3, fixing connector polarity
    [brs_flight_computer.kicad_pcb, brs_flight_computer.sch, passive_adcs.sch, switcher.sch]
2023-09-04 Integrating flight computer
    - Update FSS100 connector
    - Update secondary payload connector
    - Add pullup resistor to GaAs data
    [brs_flight_computer.kicad_pcb, passive_adcs.sch]
2023-09-04 Add load to secondary payload
    [brs_flight_computer.sch]
2023-09-05 Add silkscreen text
    [brs_flight_computer.kicad_pcb, eps_connections.sch]
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2023-09-06 Fix some tracks and update firmware
    [brs_flight_computer.kicad_pcb]
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2023-12-02 Working on flight firmware
    - Remove extra code
    - Try to fix reset
    - Check if sun sensor is working using CONL register
    - Remove no transmit flag
    - Wait for sun sensor to provide a sample
    [power.xlsx]
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

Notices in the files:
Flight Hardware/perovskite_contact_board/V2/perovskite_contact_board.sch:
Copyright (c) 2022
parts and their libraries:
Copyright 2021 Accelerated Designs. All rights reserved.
